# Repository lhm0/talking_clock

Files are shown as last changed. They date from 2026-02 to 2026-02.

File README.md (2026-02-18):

# Speaking Clock – Open Source Talking Clock for Visually Impaired Users

This repository is part of an open-source project for a simple, battery-powered **talking clock** designed for visually impaired and elderly users.

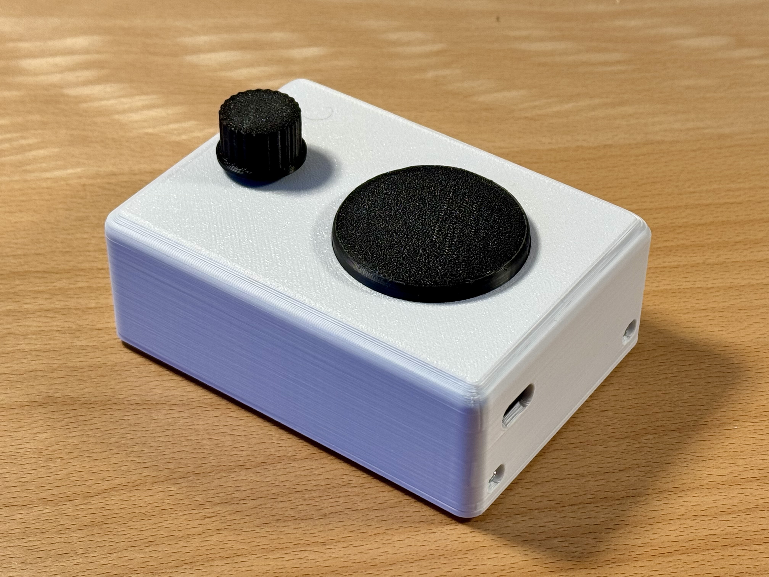
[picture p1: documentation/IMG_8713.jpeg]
Speaking Clock


The device announces the current time at the press of a button.  
If the button is pressed a second time within a short time window, it also announces the date.

Watch the full project video on YouTube:  
[Talking Clock – Demo & Build](https://youtu.be/vuX4cK3g9_s?si=J2-5so-r-MG_IsnX)

## Part of an Accessible Devices Collection

This repository is part of a small collection of **minimalistic, accessibility-focused devices for visually impaired users**. All projects follow a similar philosophy: simple operation, tactile or acoustic feedback, and a strong focus on usability and low power consumption.

The currently available devices in this collection are:

- **[DAB+ Radio](https://github.com/lhm0/DAB_minimalist)** – A minimalist, easy-to-use DAB+ radio  
- **[Talking Clock](https://github.com/lhm0/talking_clock)** – This project: a clock that announces the time acoustically  
- **[Accessible IR Remote Control](https://github.com/lhm0/accessible_ir_remote)** – A tactile, low-power TV remote control  

All projects are designed to be practical, easy to reproduce, and suitable for everyday use by visually impaired users.

## Design Goals

The main design goals of this project are:

- A **minimal and accessible user interface**
- **Fully offline operation** (no internet required)
- **Very low power consumption** for multi-year battery life
- **Simple configuration** using a smartphone via Wi-Fi
- **Low-cost hardware** based on breakout modules and a custom PCB
- A **3D-printed enclosure** for easy assembly

The clock is based on an ESP32-S3 microcontroller, uses a DS3231 real-time clock for accurate timekeeping, and plays pre-generated MP3 audio files through an I2S audio amplifier and a small speaker.  
To achieve extremely low standby power consumption, the entire system is powered only when an announcement is made.

All hardware design files, firmware, and related resources are open source and can be adapted or extended for your own projects.

---

## Time Announcement Audio Files

This repository contains **English time announcement audio files (MP3)** generated for use in the speaking clock and similar applications, systems, or projects.

These files are used as building blocks to construct spoken time and date announcements, for example:

- “The time is noon”
- “It’s one p.m.”
- “Today is Monday”

---

## License / Usage

The audio files in this repository were generated using **ttsMP3.com**.  
According to the ttsMP3 FAQ, these MP3 files may be used in personal and commercial projects without restriction (see: https://ttsmp3.com/faq).

The audio files can therefore be:

- Used in personal projects  
- Used in commercial projects  
- Shared and redistributed as part of other projects  

**Note:** This repository does not include or distribute any TTS software or voices themselves, only the generated audio files.

---

## About

These audio files are intended to be used as building blocks for English time announcements in embedded projects such as the Speaking Clock.

If you use this repository, please make sure to check the current terms of ttsMP3.com to ensure compliance with their conditions.

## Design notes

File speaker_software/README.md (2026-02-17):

# Speaker Software (ESP32-S3 Pico)

This folder contains the ESP32-S3 implementation.

## Structure

- `platformio.ini` - PlatformIO environments and build flags
- `src/` - Application entry point (`main.cpp`)
- `include/` - Project-wide config and board pin maps
- `lib/` - Reusable modules (hardware abstraction + device drivers)
- `test/` - Placeholder for unit tests
- `docs/` - Notes and integration docs

## Modules

- `lib/hal/` - Hardware abstraction interfaces
- `lib/time_speech/` - Time/date playlist generators + timezone/DST
- `lib/rtc_ds3231/` - DS3231 RTC driver

## Notes

- Audio files are stored in LittleFS under `/mp3`.
- Audio uses ESP8266Audio (legacy i2s.h backend).

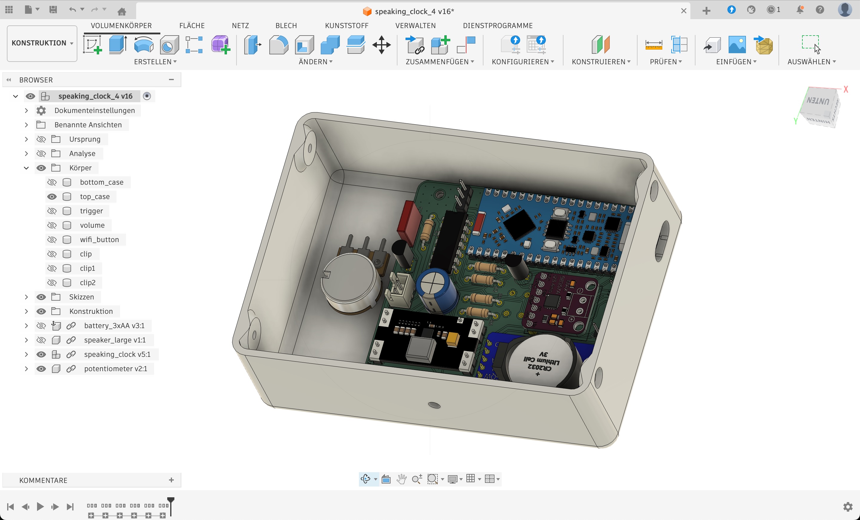
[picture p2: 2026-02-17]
documentation/mech_design3.jpg

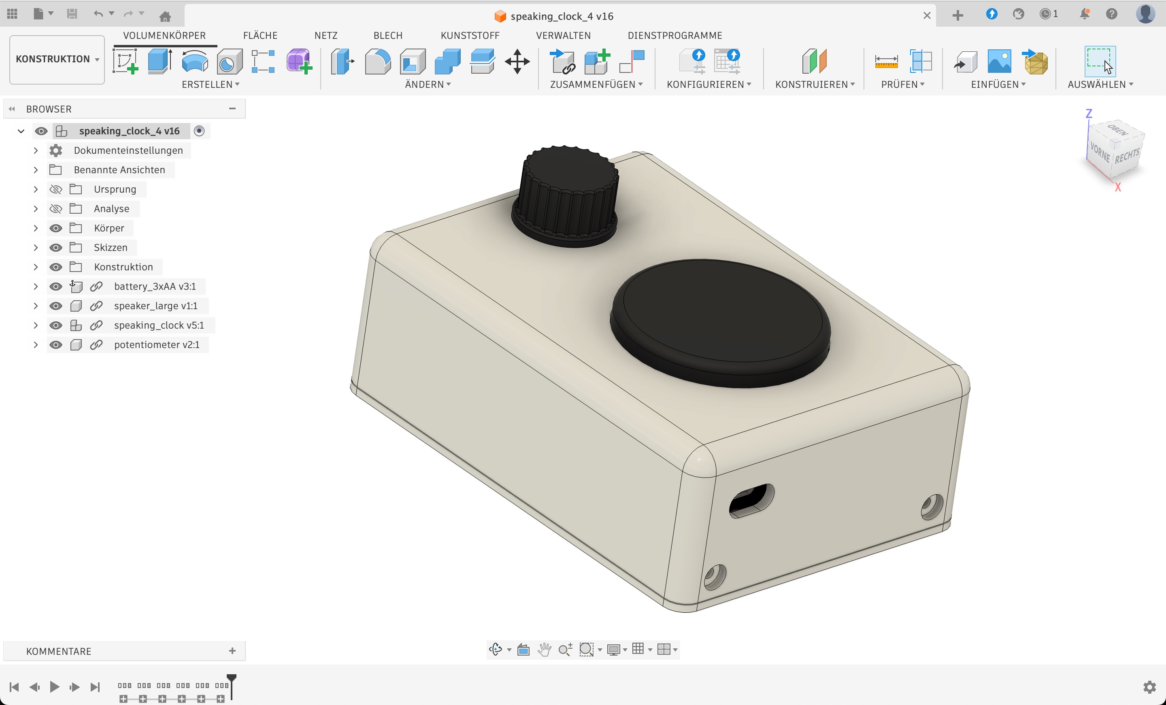
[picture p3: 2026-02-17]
documentation/mech_design1.jpg

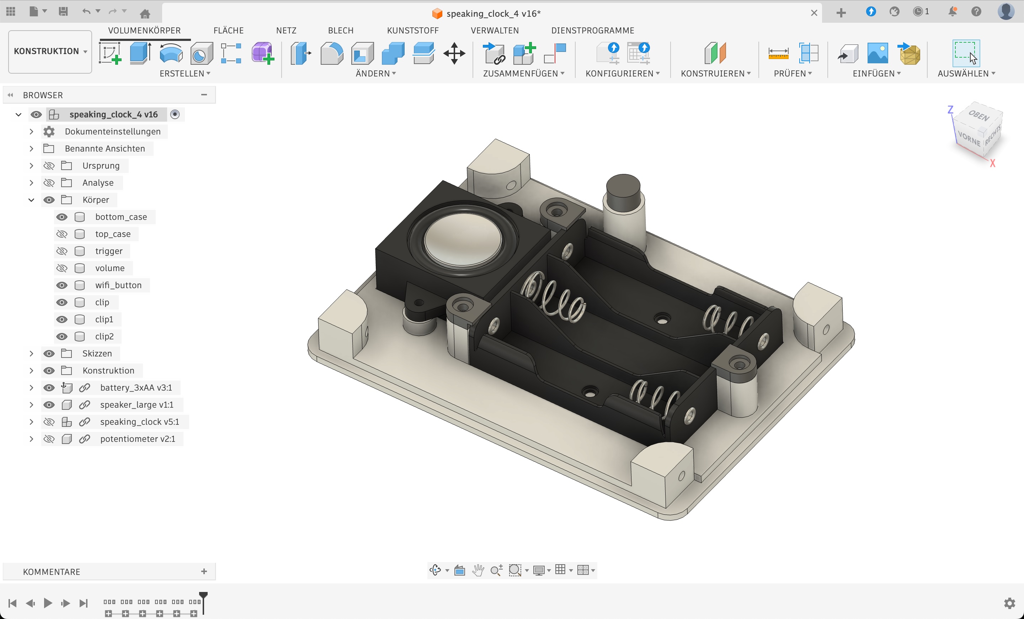
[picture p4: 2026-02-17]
documentation/mech_design2.jpg

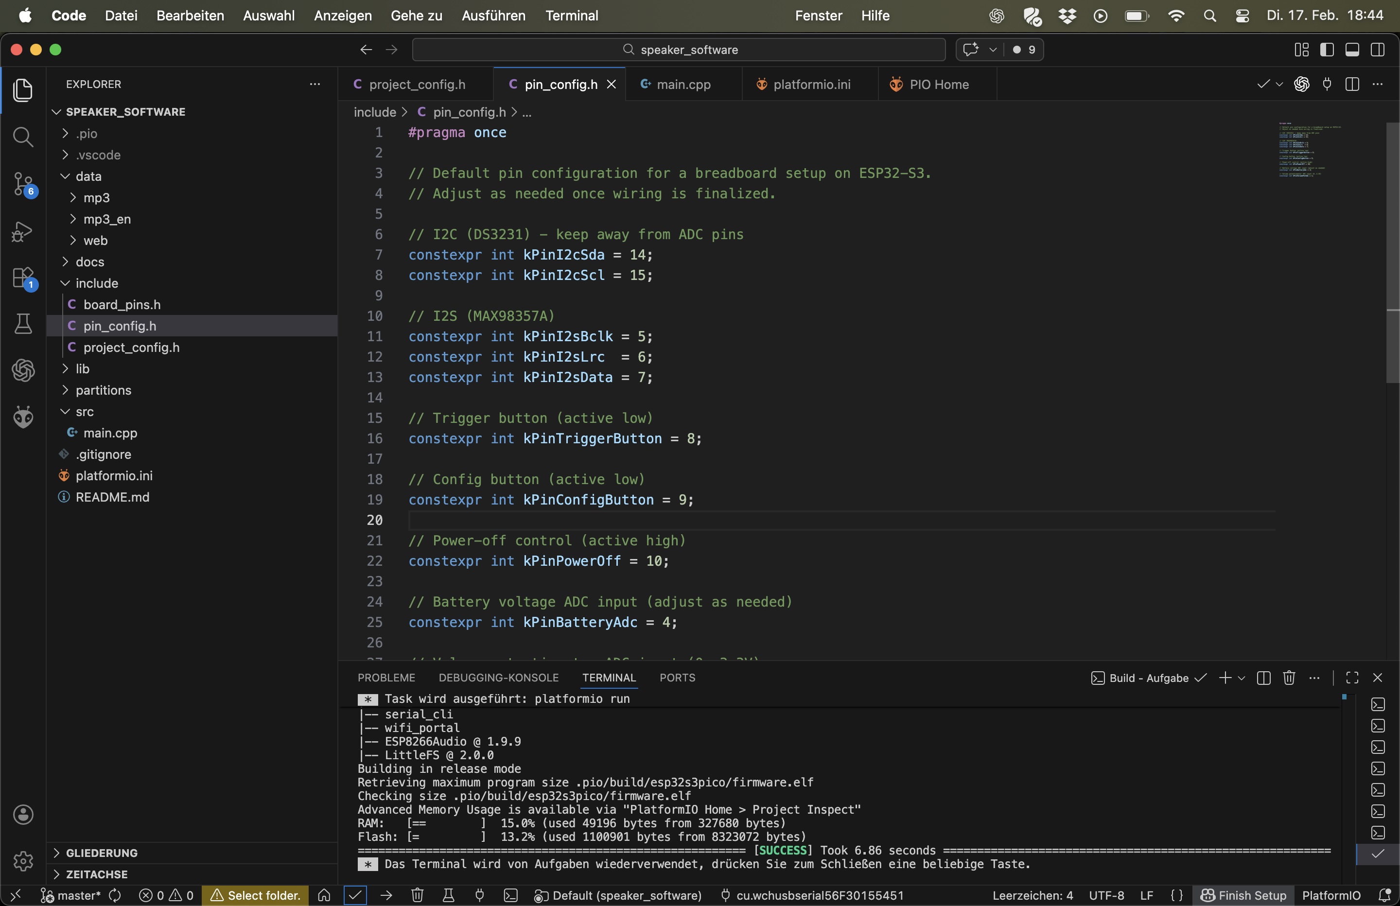
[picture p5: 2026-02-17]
documentation/VS_Code.jpg

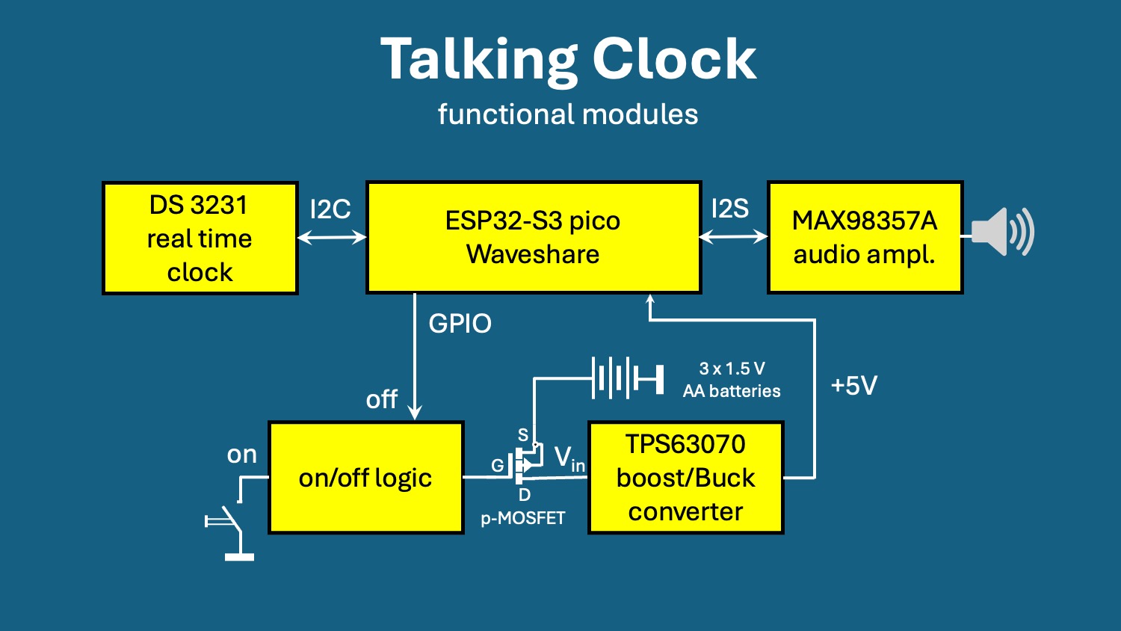
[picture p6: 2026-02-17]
documentation/functional blocks.jpg

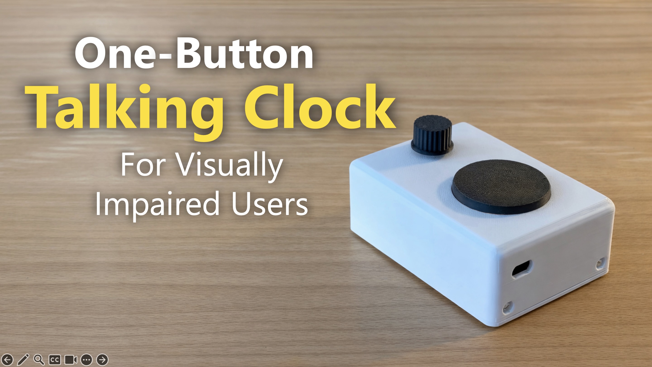
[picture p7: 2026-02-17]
documentation/thumbnail.jpg

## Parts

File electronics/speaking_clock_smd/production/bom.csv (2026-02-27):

Designator | Footprint | Quantity | Value | LCSC Part #
BT1 | Keytone_CR2032_holder | 1 | CR2032
C1, C10, C11, C13, C16, C19, C2, C24, C27, C29, C31, C8 | 0402 | 12 | 100nF | C307331
C12 | 0402 | 1 | 10nF | C15195
C14, C15, C17, C9 | 0402 | 4 | 1µF | C52923
C18, C22, C23, C3 | 0603 | 4 | 10µF | C96446
C20, C21, C30 | 0805 | 3 | 10µF | C15850
C25, C26 | 0805 | 2 | 22µF | C45783
C28 | 0603 | 1 | 1nF | C1588
C4, C6 | 0402 | 2 | 10pF | C32949
C5, C7 | 0402 | 2 | 3p3 | C1565
D1, D2 | D_SMA | 2 | SS24 | C7420362
D3 | 0603 | 1 | LED | C2286
J1 | USB_C_Receptacle | 1 | USB_C_Receptacle_USB2.0 | C709357
J2 | JST_XH_B2B-XH-A_1x02_P2.50mm_Vertical | 1 | Conn_01x02_Pin
J3 | 3_pin_jumper | 1 | Conn_01x03_Pin
J4 | 2_pin | 1 | Conn_01x02_Pin
L1, L2 | 0402 | 2 | 2n2 | C412264
L3 | L_Bourns_SRP7028A_7.3x6.6mm | 1 | 2.2µH | C167218
Q1 | SOT-23 | 1 | IRLML6401 | C382329
Q2, Q3 | SOT-23 | 2 | AO3400A | C20917
R1, R2 | 0402 | 2 | 5k1 | C25905
R10, R11, R12, R13, R17, R18, R19 | 0402 | 7 | 10k | C25744
R14 | 0402 | 1 | 20k | C25765
R15, R16 | 0402 | 2 | 4k7 | C25900
R20, R21, R22, R23, R28, R3 | 0402 | 6 | 100k | C25741
R24 | 0603 | 1 | 470k | C23178
R25 | 0603 | 1 | 150k | C22807
R26 | 0603 | 1 | 1k | C21190
R27 | 0402 | 1 | 2k2 | C25879
R4, R5, R6, R7, R8 | 0402 | 5 | 0 | C17168
R9 | 0402 | 1 | 22 | C25092
SW1 | C720477 | 1 | reset | C720477
SW2 | RotaryEncoder_Alps_EC11E-Switch_Vertical_H20mm | 1 | volume_knob
SW3 | OmronTaster | 1 | config
U1 | SOIC-8_5.3x5.3mm_P1.27mm | 1 | W25Q128JVS | C97521
U2 | SOT-23-6 | 1 | USBLC6-2SC6 | C2687116
U20, U21, U22 | JLC_tooling_hole | 3 | ~
U3 | PCB_antenna | 1 | WiFi antenna
U4 | IC_ESP32-S3 | 1 | ESP32-S3 | C2913192
U5 | 1pin | 1 | ~
U6 | SOIC-14_3.9x8.7mm_P1.27mm | 1 | HEF4093B | C7867
U7 | VREG_TPS63070RNMR | 1 | TPS63070RNMR | C109322
U8 | SOIC-8_3.9x4.9mm_P1.27mm | 1 | DS3231MZ | C107410
U9 | TQFN-16-1EP_3x3mm_P0.5mm_EP1.23x1.23mm | 1 | MAX98357A | C910544
Y1 | Crystal_SMD_4Pin_3.2x2.5mm | 1 | 40 MHz | C379787

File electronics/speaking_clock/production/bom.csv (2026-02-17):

Designator | Footprint | Quantity | Value | LCSC Part #
A1 | Waveshare_ESP32_S3_pico | 1 | Waveshare_ESP32-S3_Pico
C1 | CP_Radial_D6.3mm_P2.50mm | 1 | 220µF, 16V
C2, C3 | C_Rect_L10.0mm_W2.5mm_P7.50mm_MKS4 | 2 | 100nF
D1 | LED_D3.0mm | 1 | LED
J1 | JST_XH_B2B-XH-A_1x02_P2.50mm_Vertical | 1 | Conn_01x02_Pin
J2, J4 | 3_pin_jumper | 2 | Conn_01x03_Pin
J3 | 2_pin | 1 | Conn_01x02_Pin
Q1, Q2 | TO-92L_Inline | 2 | 2N7000
Q3 | SOT-23 | 1 | IRLML6401
R1, R2, R3 | R_Axial_DIN0207_L6.3mm_D2.5mm_P10.16mm_Horizontal | 3 | 100k | C25768
R4 | R_Axial_DIN0207_L6.3mm_D2.5mm_P10.16mm_Horizontal | 1 | 1k
R5 | R_Axial_DIN0207_L6.3mm_D2.5mm_P10.16mm_Horizontal | 1 | 1M
R6 | R_Axial_DIN0207_L6.3mm_D2.5mm_P10.16mm_Horizontal | 1 | 2M
SW1 | OmronTaster | 1 | ON
SW2 | OmronTaster | 1 | config
U1 | TPS63070_breakout | 1 | TPS63070
U2 | DIP-14_W7.62mm | 1 | HEF4093B
U3 | MAX98357A_breakout | 1 | MAX98357A
U4 | DS3231 | 1 | DS3231

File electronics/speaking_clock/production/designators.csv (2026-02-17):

A1:1
C1:1
C2:1
C3:1
D1:1
J1:1
J2:1
J3:1
J4:1
Q1:1
Q2:1
Q3:1
R1:1
R2:1
R3:1
R4:1
R5:1
R6:1
SW1:1
SW2:1
U1:1
U2:1
U3:1
U4:1

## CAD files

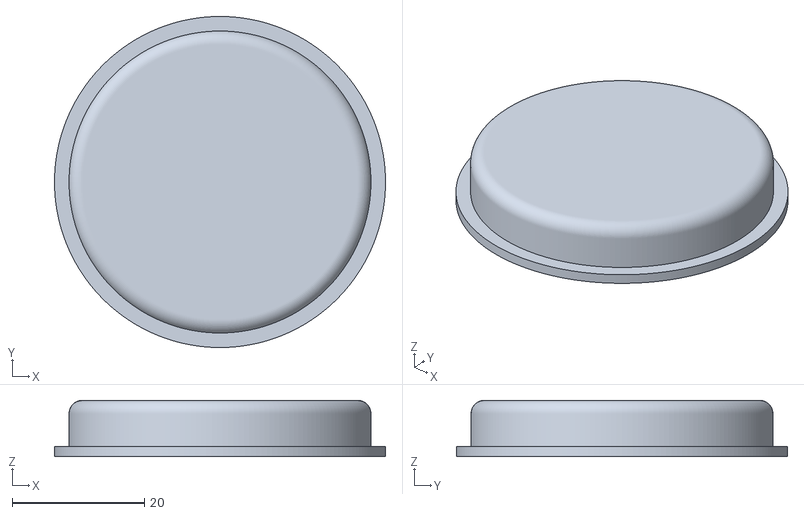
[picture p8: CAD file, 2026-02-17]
mechanical_design/trigger.stl
50.0 x 50.0 x 8.50

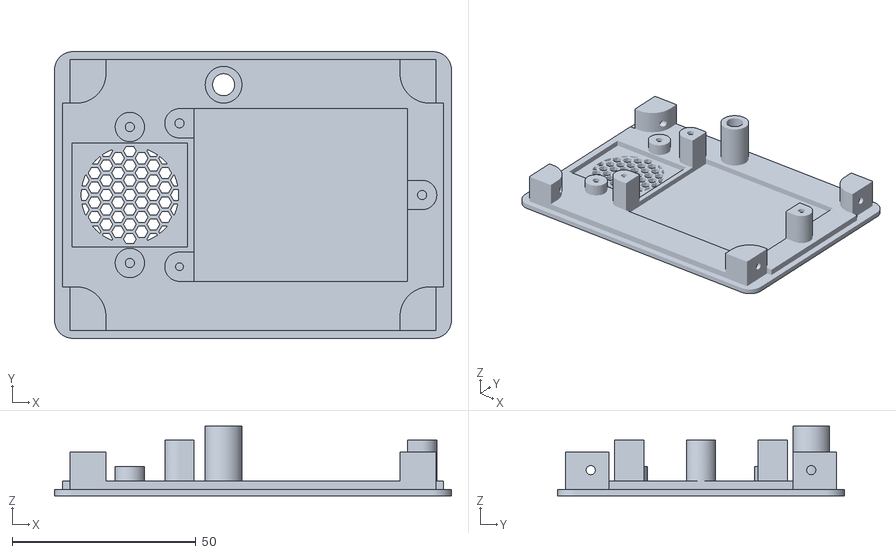
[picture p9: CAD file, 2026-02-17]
mechanical_design/bottom_case.stl
108.0 x 78.0 x 19.0

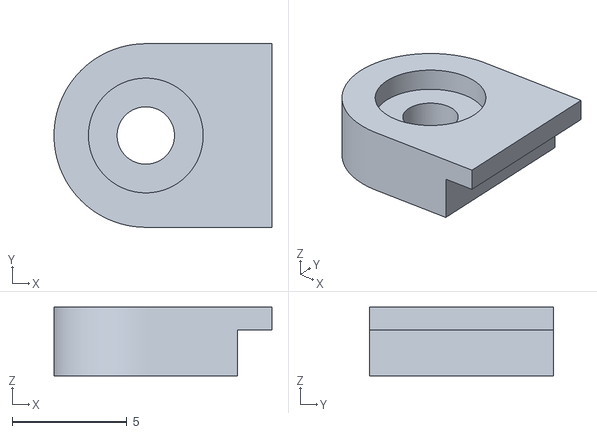
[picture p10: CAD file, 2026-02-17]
mechanical_design/clip2.stl
9.50 x 8.00 x 3.00

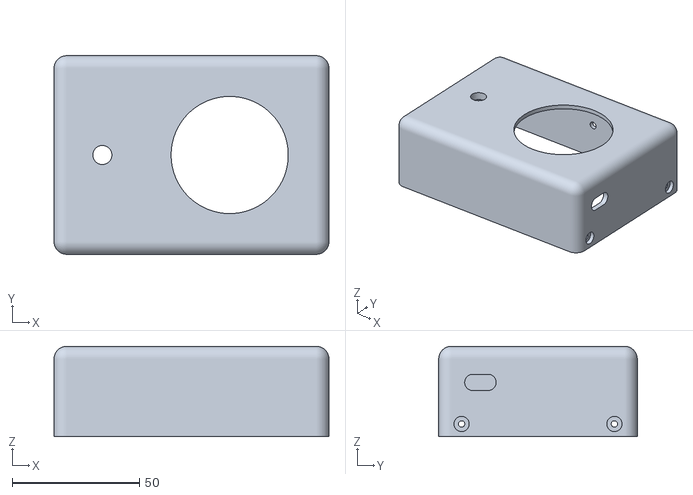
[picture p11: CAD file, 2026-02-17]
mechanical_design/top_case.stl
108.0 x 78.0 x 35.5

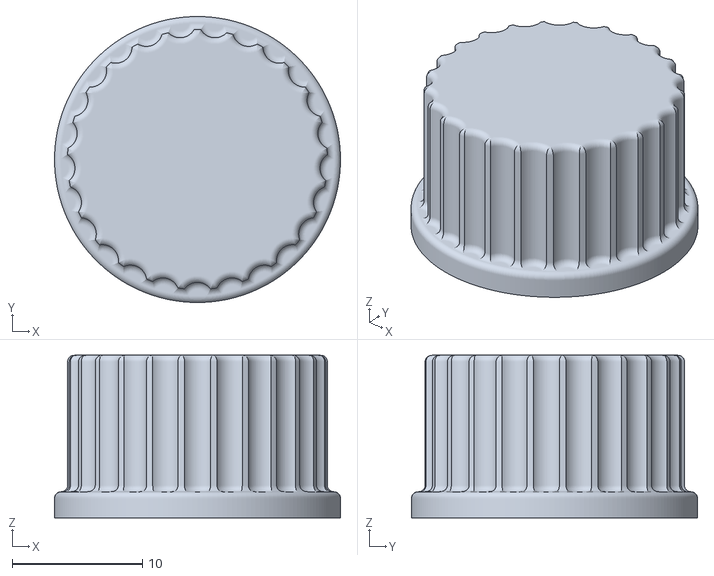
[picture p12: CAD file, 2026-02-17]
mechanical_design/volume.stl
22.0 x 22.0 x 12.5

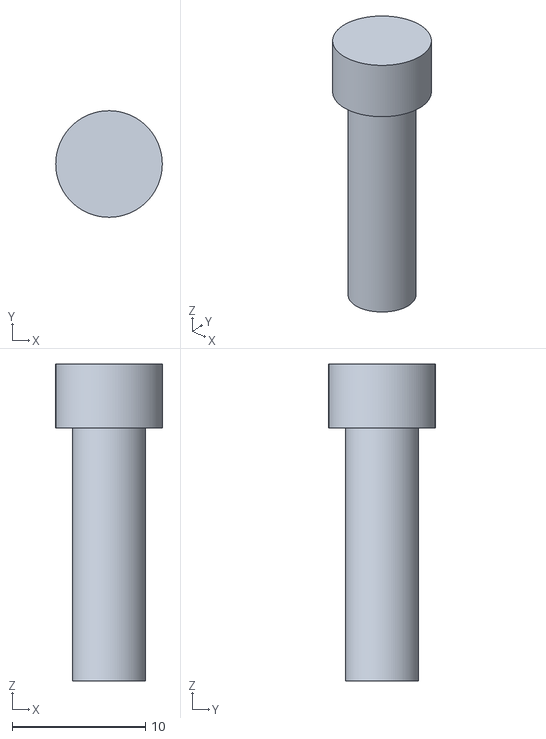
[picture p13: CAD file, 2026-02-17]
mechanical_design/wifi_button.stl
8.00 x 8.00 x 23.8

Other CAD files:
mechanical_design/clip1.stl
mechanical_design/clip.stl

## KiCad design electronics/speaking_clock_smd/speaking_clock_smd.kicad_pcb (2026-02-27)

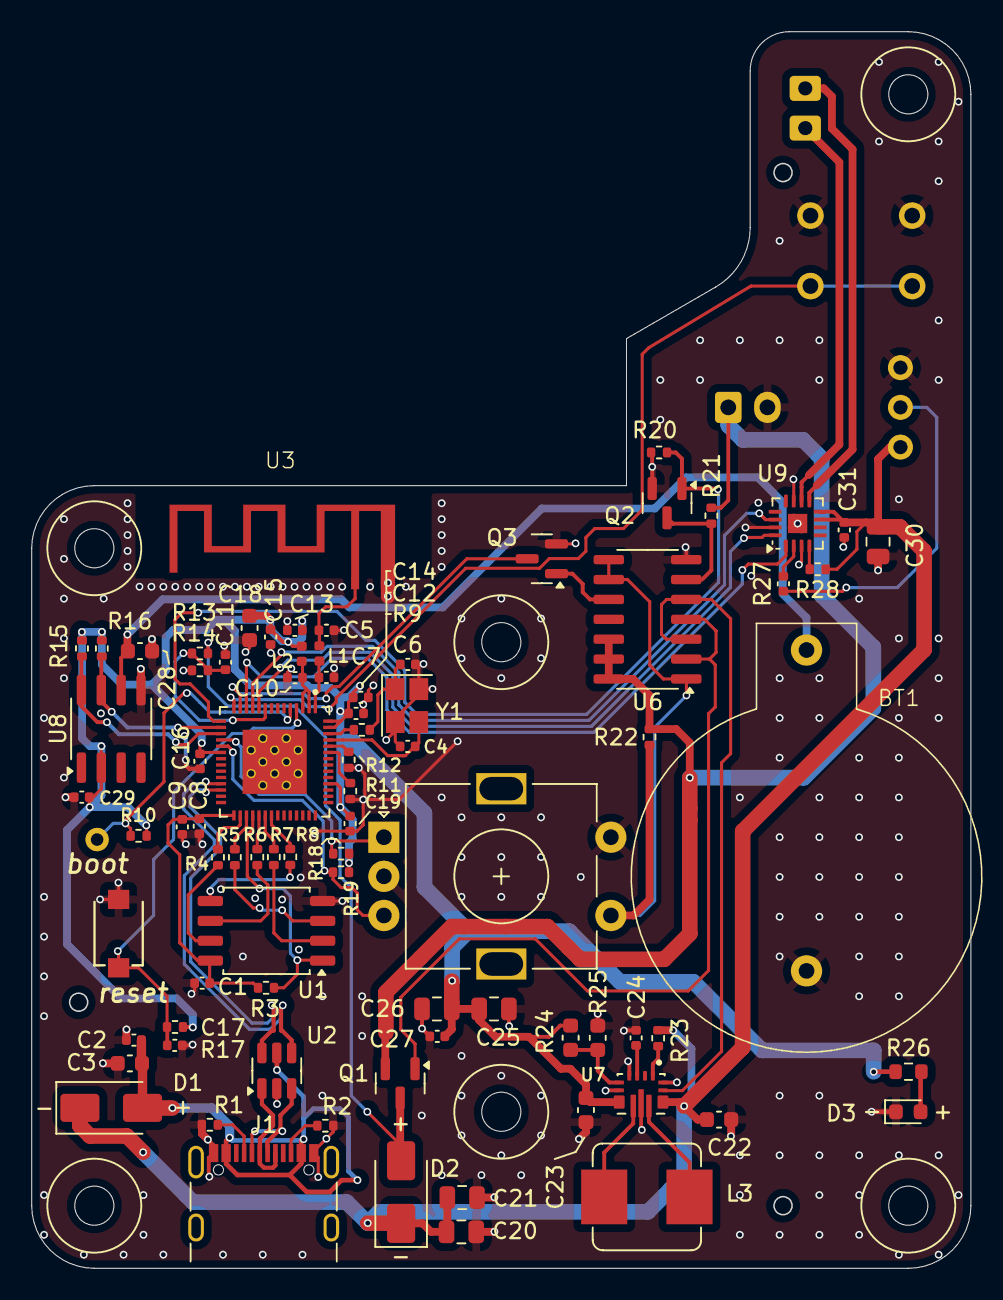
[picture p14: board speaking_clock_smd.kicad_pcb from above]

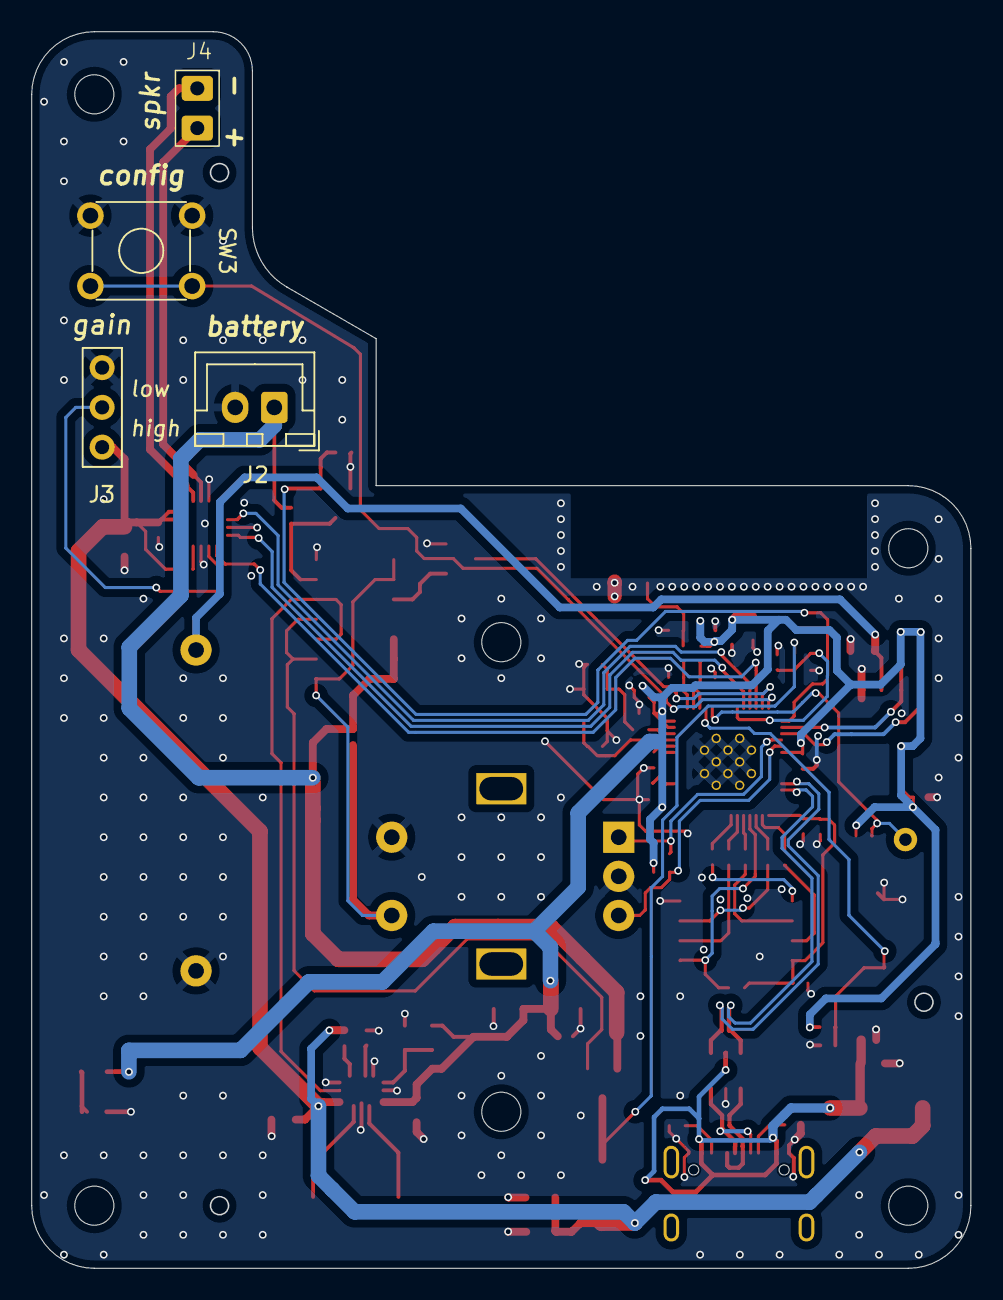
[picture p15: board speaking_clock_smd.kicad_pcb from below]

Board: 4 copper layers, 60.0 x 79.0 mm, 89 parts (4 on the bottom side), 62 nets.

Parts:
BT1: CR2032; Keytone_CR2032_holder
C1, C2, C8, C10, C11, C13, C16, C19, C24, C27, C29, C31: 100nF; C_0402_1005Metric
C3, C18, C22, C23: 10µF; C_0603_1608Metric
C4, C6: 10pF; C_0402_1005Metric
C5, C7: 3p3; C_0402_1005Metric
C9, C14, C15, C17: 1µF; C_0402_1005Metric
C12: 10nF; C_0402_1005Metric
C20, C21, C30: 10µF; C_0805_2012Metric
C25, C26: 22µF; C_0805_2012Metric
C28: 1nF; C_0603_1608Metric
D1, D2: SS24; D_SMA
D3: LED; LED_0603_1608Metric
J1: USB_C_Receptacle_USB2.0; USB_C_Receptacle
J2: Conn_01x02_Pin; JST_XH_B2B-XH-A_1x02_P2.50mm_Vertical
J3: Conn_01x03_Pin; 3_pin_jumper
J4: Conn_01x02_Pin; 2_pin
L1, L2: 2n2; L_0402_1005Metric
L3: 2.2µH; L_Bourns_SRP7028A_7.3x6.6mm
Q1: IRLML6401; SOT-23
Q2, Q3: AO3400A; SOT-23
R1, R2: 5k1; R_0402_1005Metric
R3, R20, R21, R22, R23, R28: 100k; R_0402_1005Metric
R4, R5, R6, R7, R8: 0; R_0402_1005Metric
R9: 22; R_0402_1005Metric
R10, R11, R12, R13, R17, R18, R19: 10k; R_0402_1005Metric
R14: 20k; R_0402_1005Metric
R15, R16: 4k7; R_0402_1005Metric
R24: 470k; C_0603_1608Metric
R25: 150k; C_0603_1608Metric
R26: 1k; R_0603_1608Metric
R27: 2k2; C_0402_1005Metric
SW1: reset; C720477
SW2: volume_knob; RotaryEncoder_Alps_EC11E-Switch_Vertical_H20mm
SW3: config; OmronTaster
U1: W25Q128JVS; SOIC-8_5.3x5.3mm_P1.27mm
U2: USBLC6-2SC6; SOT-23-6
U3: WiFi antenna; PCB_antenna
U4: ESP32-S3; IC_ESP32-S3
U5: 1pin
U6: HEF4093B; SOIC-14_3.9x8.7mm_P1.27mm
U7: TPS63070RNMR; VREG_TPS63070RNMR
U8: DS3231MZ; SOIC-8_3.9x4.9mm_P1.27mm
U9: MAX98357A; TQFN-16-1EP_3x3mm_P0.5mm_EP1.23x1.23mm
U20, U21, U22: JLC_tooling_hole
Y1: 40 MHz; Crystal_SMD_4Pin_3.2x2.5mm

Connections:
+3.3V: C12.1, C13.1, C14.1, C15.1, C16.1, C18.1, C19.1, C23.2, C25.1, C26.1, C27.1, C29.1, L2.2, R10.2, R15.2, R16.2, R17.1, R18.2, R19.1, R24.1, R26.1, U4.20 (VDD3P3_RTC), U4.46 (VDD3P3_CPU), U4.55 (VDDA1), U4.56 (VDDA2), U7.7_8 (VOUT), U8.2 (VCC)
/ESP32-S3 microcontroller/A5: J1.A5 (CC1), R1.1
/ESP32-S3 microcontroller/B5: J1.B5 (CC2), R2.1
/ESP32-S3 microcontroller/EN: C17.1, R17.2, SW1.1, U4.4 (CHIP_PU)
/ESP32-S3 microcontroller/ESP_D+: J1.A6 (D+), J1.B6 (D+), U2.1 (I/O1)
/ESP32-S3 microcontroller/ESP_D-: J1.A7 (D-), J1.B7 (D-), U2.3 (I/O2)
/ESP32-S3 microcontroller/GPIO4: C11.1, R13.2, R14.1, U4.9 (GPIO4)
/ESP32-S3 microcontroller/GPIO45: R11.1, U4.51 (GPIO45)
/ESP32-S3 microcontroller/GPIO46: R12.1, U4.52 (GPIO46)
/ESP32-S3 microcontroller/LNA: C7.1, L1.2, U4.1 (LNA_IN)
/ESP32-S3 microcontroller/SPICLK: R6.1, U1.6 (CLK)
/ESP32-S3 microcontroller/SPICLK_: R6.2, U4.33 (SPICLK)
/ESP32-S3 microcontroller/SPICS0: R3.1, U1.1 (~CS), U4.32 (SPICS0)
/ESP32-S3 microcontroller/SPID: R8.1, U1.5 (DI(IO0))
/ESP32-S3 microcontroller/SPID_: R8.2, U4.35 (SPID)
/ESP32-S3 microcontroller/SPIHD: R4.1, U1.7 (IO3)
/ESP32-S3 microcontroller/SPIHD_: R4.2, U4.30 (SPIHD)
/ESP32-S3 microcontroller/SPIQ: R7.1, U1.2 (DO(IO1))
/ESP32-S3 microcontroller/SPIQ_: R7.2, U4.34 (SPIQ)
/ESP32-S3 microcontroller/SPIWP: R5.1, U1.3 (IO2)
/ESP32-S3 microcontroller/SPIWP_: R5.2, U4.31 (SPIWP)
/ESP32-S3 microcontroller/UD_ESP+: U2.6 (I/O1), U4.26 (GPIO20)
/ESP32-S3 microcontroller/UD_ESP-: U2.4 (I/O2), U4.25 (GPIO19)
/ESP32-S3 microcontroller/VBUS3: C2.2, C3.1, D1.2 (A), J1.A4 (VBUS), J1.A9 (VBUS), J1.B4 (VBUS), J1.B9 (VBUS), U2.5 (VBUS)
/ESP32-S3 microcontroller/VDD3P3: C10.1, L2.1, U4.2 (VDD3P3), U4.3 (VDD3P3)
/ESP32-S3 microcontroller/VDD_SPI: C1.2, C8.1, C9.1, R3.2, U1.8 (VCC), U4.29 (VDD_SPI)
/ESP32-S3 microcontroller/XTAL_N: C4.1, U4.53 (XTAL_N), Y1.3
/ESP32-S3 microcontroller/XTAL_P: R9.2, U4.54 (XTAL_P)
/ESP32-S3 microcontroller/XTAL_Pp: C6.1, R9.1, Y1.1
/ESP32-S3 microcontroller/boot: R10.1, U4.5 (GPIO0), U5.1 (pin)
/ESP32-S3 microcontroller/feed: C5.1, L1.1, U3.2 (feed)
/peripherals/FB: R24.2, R25.1, U7.5 (FB)
/peripherals/Gain: R27.2, U9.2 (GAIN_SLOT)
/peripherals/Gain_Jumper: J3.2, R27.1
/peripherals/L1: L3.2, U7.11 (L1)
/peripherals/L2: L3.1, U7.9 (L2)
/peripherals/PS/SYNC: R23.2, U7.1 (PS/SYNC)
/peripherals/VAUX: C24.2, U7.3 (VAUX)
/peripherals/spkr_+: J4.2, U9.10 (OUTN)
/peripherals/spkr_-: J4.1, U9.9 (OUTP)
/peripherals//OFF: Q2.3 (D), R21.1, U6.6
/peripherals//ON: Q3.1 (G), U6.10
/peripherals//SD: R28.1, U9.4 (~SD_MODE)
GND: BT1.2 (-), C1.1, C2.1, C3.2, C4.2, C5.2, C6.2, C7.2, C8.2, C9.2, C10.2, C11.2, C12.2, C13.2, C14.2, C15.2, C16.2, C17.2, C18.2, C19.2, C20.2, C21.2, C22.1, C23.1, C24.1, C25.2, C26.2, C27.2, C28.1, C29.2, C30.2, C31.2, D3.1 (K), J1.A1 (GND), J1.A12 (GND), J1.B1 (GND), J1.B12 (GND), J2.2, J3.3, Q2.2 (S), Q3.2 (S), R1.2, R2.2, R11.2, R12.2, R14.2, R20.1, R25.2, SW1.2, SW2.C, SW2.S2, SW3.1 (A), U1.4 (GND), U2.2 (GND), U3.1 (GND), U4.57 (GND), U4.58 (GND), U4.59 (GND), U4.60 (GND), U4.61 (GND), U4.62 (GND), U4.63 (GND), U4.64 (GND), U4.65 (GND), U4.66 (GND), U4.67 (GND), U4.68 (GND), U4.69 (GND), U6.7 (GND), U7.4 (GND), U7.6 (FB2), U7.10 (PGND), U7.15 (VSEL), U8.5 (GND), U9.3 (GND), U9.11 (GND), U9.15 (GND), U9.17 (PAD), Y1.2, Y1.4
I2C_SCL: R15.1, U4.17 (GPIO12), U8.8 (SCL)
I2C_SDA: R16.1, U4.16 (GPIO11), U8.7 (SDA)
I2S_BCLK: U4.10 (GPIO5), U9.16 (BCLK)
I2S_DIN: U4.12 (GPIO7), U9.1 (DIN)
I2S_LRC: U4.11 (GPIO6), U9.14 (LRCLK)
unnamed: BT1.1 (+), C28.2, U8.6 (VBAT)
unnamed: D3.2 (A), R26.2
OFF: Q2.1 (G), R20.2, U4.15 (GPIO10)
ON: R22.1, SW2.S1, U6.1, U6.8, U6.9
VBat: J2.1, Q1.2 (S), R21.2, R22.2, U6.12, U6.13, U6.14 (VCC)
VBat_s: D2.2 (A), Q1.3 (D), R13.1
VIN: C20.1, C21.1, C22.2, C30.1, C31.1, D1.1 (K), D2.1 (K), J3.1, R23.1, R28.2, U7.12_13 (VIN), U9.7 (VDD), U9.8 (VDD)
config: SW3.2 (B), U4.14 (GPIO9)
enable: U6.3, U6.5, U7.14 (EN)
rotary_A: R18.1, SW2.A, U4.18 (GPIO13)
rotary_B: R19.2, SW2.B, U4.19 (GPIO14)
trigger: Q3.3 (D), U4.13 (GPIO8)
/enable: Q1.1 (G), U6.2, U6.4

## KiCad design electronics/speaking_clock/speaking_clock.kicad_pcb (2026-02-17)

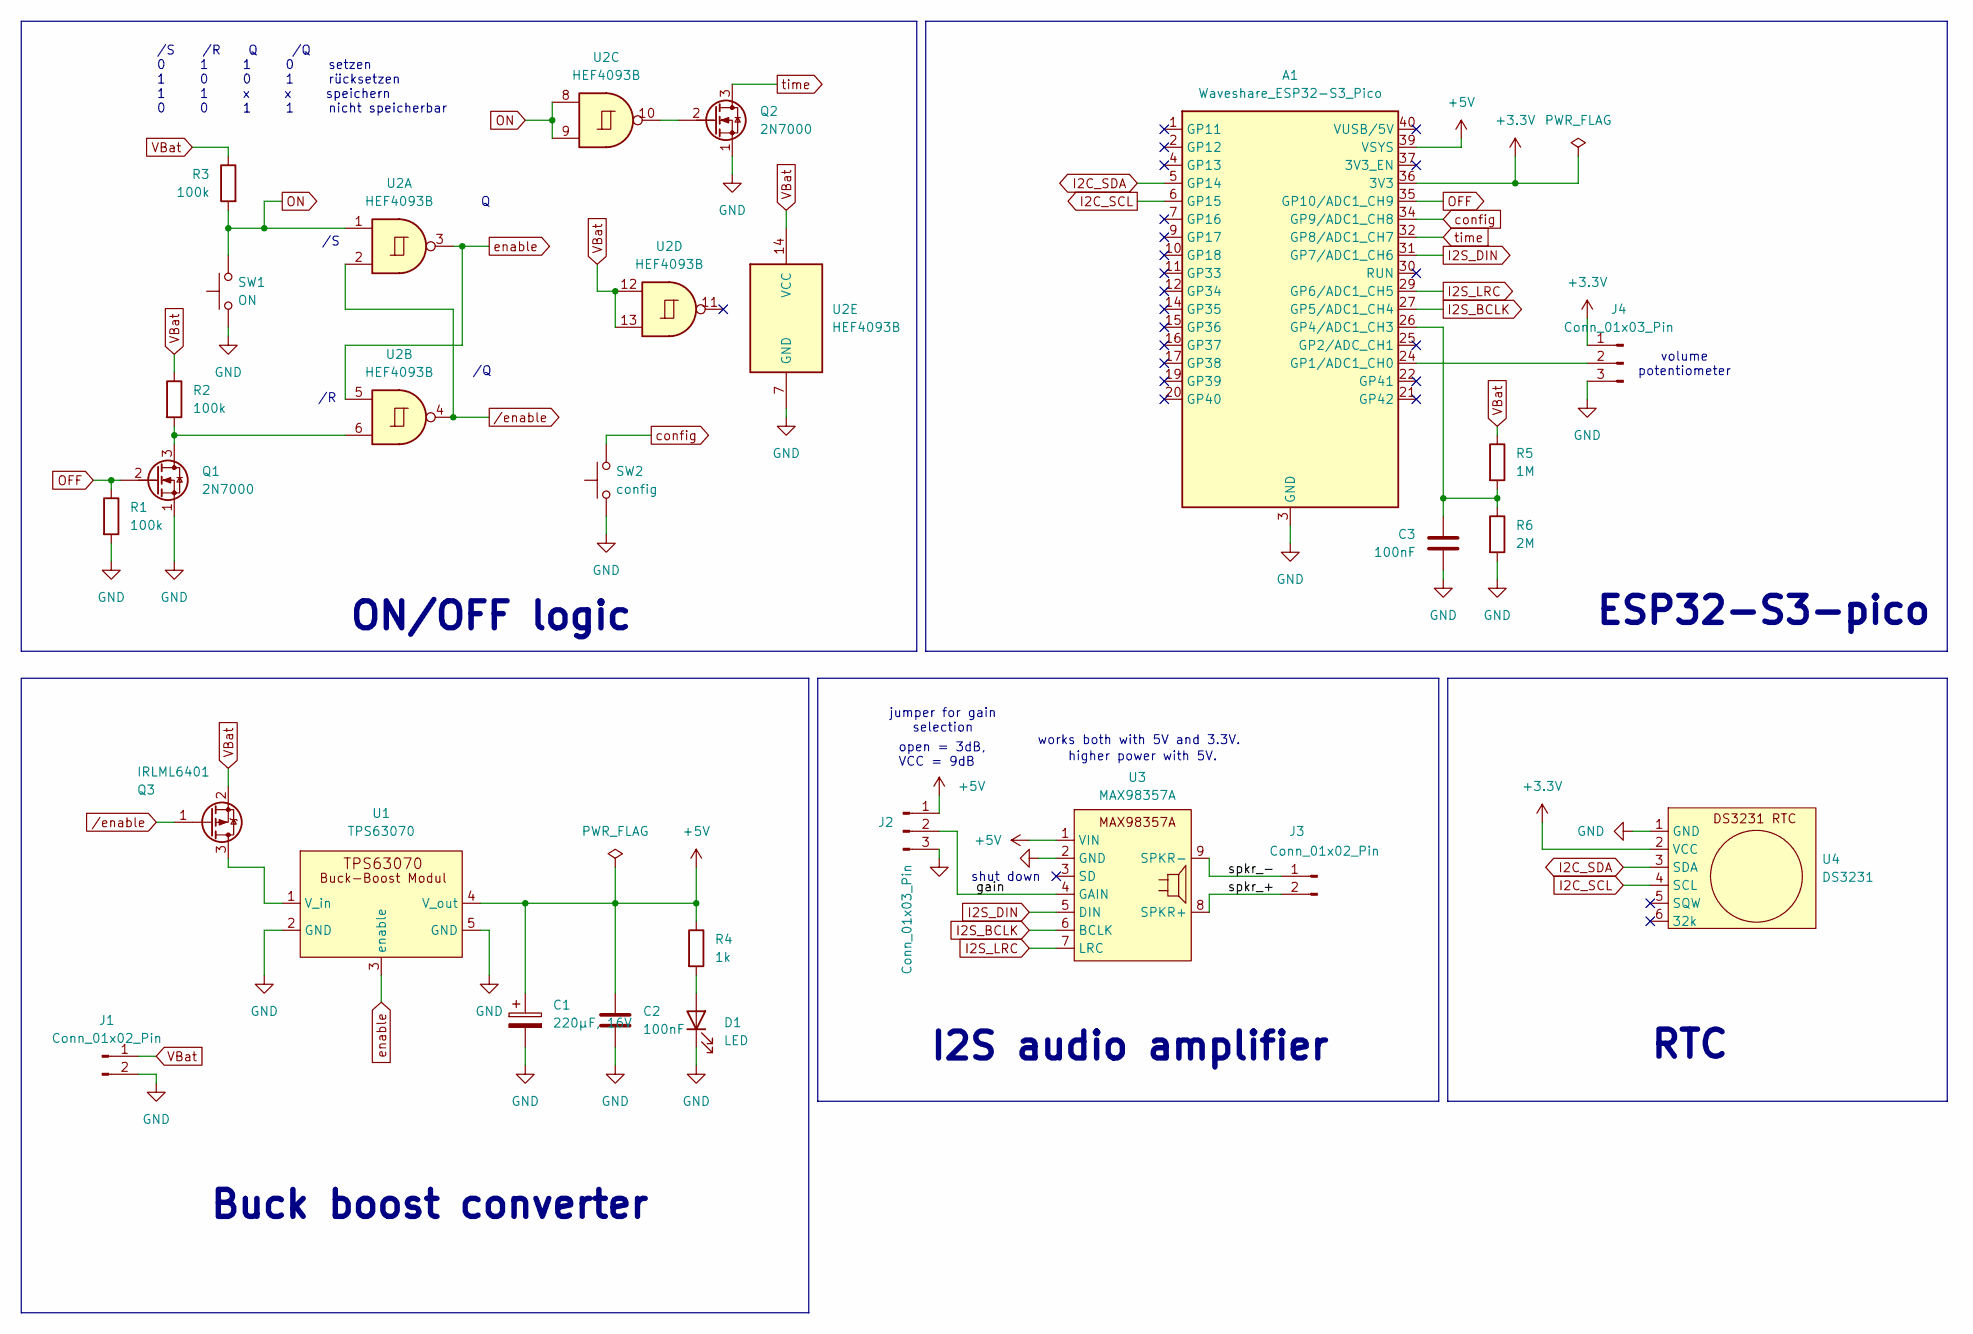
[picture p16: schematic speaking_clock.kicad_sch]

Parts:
A1: Waveshare_ESP32-S3_Pico; Waveshare_ESP32_S3_pico
C1: 220µF, 16V; CP_Radial_D6.3mm_P2.50mm
C2, C3: 100nF; C_Rect_L10.0mm_W2.5mm_P7.50mm_MKS4
D1: LED; LED_D3.0mm
J1: Conn_01x02_Pin; JST_XH_B2B-XH-A_1x02_P2.50mm_Vertical
J2, J4: Conn_01x03_Pin; 3_pin_jumper
J3: Conn_01x02_Pin; 2_pin
Q1, Q2: 2N7000; TO-92L_Inline
Q3: IRLML6401; SOT-23
R1, R2, R3: 100k; R_Axial_DIN0207_L6.3mm_D2.5mm_P10.16mm_Horizontal; LCSC C25768
R4: 1k; R_Axial_DIN0207_L6.3mm_D2.5mm_P10.16mm_Horizontal
R5: 1M; R_Axial_DIN0207_L6.3mm_D2.5mm_P10.16mm_Horizontal
R6: 2M; R_Axial_DIN0207_L6.3mm_D2.5mm_P10.16mm_Horizontal
SW1: ON; OmronTaster
SW2: config; OmronTaster
U1: TPS63070; TPS63070_breakout
U2: HEF4093B; DIP-14_W7.62mm
U3: MAX98357A; MAX98357A_breakout
U4: DS3231

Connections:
+3.3V: A1.36 (3V3), J4.1, U4.2 (VCC), U4.9 (VCC)
+5V: A1.39 (VSYS), C1.1, C2.1, J2.1, R4.1, U1.4 (V_out), U3.1 (VIN)
/gain: J2.2, U3.4 (GAIN)
/spkr_+: J3.2, U3.8 (SPKR+)
/spkr_-: J3.1, U3.9 (SPKR-)
GND: A1.3 (GND), A1.8 (GND), A1.13 (GND), A1.18 (GND), A1.23 (GND), A1.28 (GND), A1.33 (GND), A1.38 (GND), C1.2, C2.2, C3.2, D1.1 (K), J1.2, J2.3, J4.3, Q1.1 (S), Q2.1 (S), R1.2, R6.2, SW1.1 (A), SW2.1 (A), U1.2 (GND), U1.5 (GND), U2.7 (GND), U3.2 (GND), U4.1 (GND), U4.10 (GND)
I2C_SCL: A1.6 (GP15), U4.4 (SCL), U4.7 (SCL)
I2C_SDA: A1.5 (GP14), U4.3 (SDA), U4.8 (SDA)
I2S_BCLK: A1.27 (GP5/ADC1_CH4), U3.6 (BCLK)
I2S_DIN: A1.31 (GP7/ADC1_CH6), U3.5 (DIN)
I2S_LRC: A1.29 (GP6/ADC1_CH5), U3.7 (LRC)
unnamed: A1.24 (GP1/ADC1_CH0), J4.2
unnamed: A1.26 (GP4/ADC1_CH3), C3.1, R5.2, R6.1
unnamed: D1.2 (A), R4.2
unnamed: Q1.3 (D), R2.2, U2.6
unnamed: Q2.2 (G), U2.10
unnamed: Q3.3 (D), U1.1 (V_in)
OFF: A1.35 (GP10/ADC1_CH9), Q1.2 (G), R1.1
ON: R3.2, SW1.2 (B), U2.1, U2.8, U2.9
VBat: J1.1, Q3.2 (S), R2.1, R3.1, R5.1, U2.12, U2.13, U2.14 (VCC)
config: A1.34 (GP9/ADC1_CH8), SW2.2 (B)
enable: U1.3 (enable), U2.3, U2.5
time: A1.32 (GP8/ADC1_CH7), Q2.3 (D)
/enable: Q3.1 (G), U2.2, U2.4

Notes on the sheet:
/S /R Q /Q 0 1 1 0 setzen 1 0 0 1 rücksetzen 1 1 x x speichern 0 0 1 1 nicht speicherbar
open = 3dB, VCC = 9dB
I2S audio amplifier
ESP32-S3-pico
jumper for gain selection
works both with 5V and 3.3V.
RTC
higher power with 5V.
Buck boost converter
shut down
ON/OFF logic
volume potentiometer

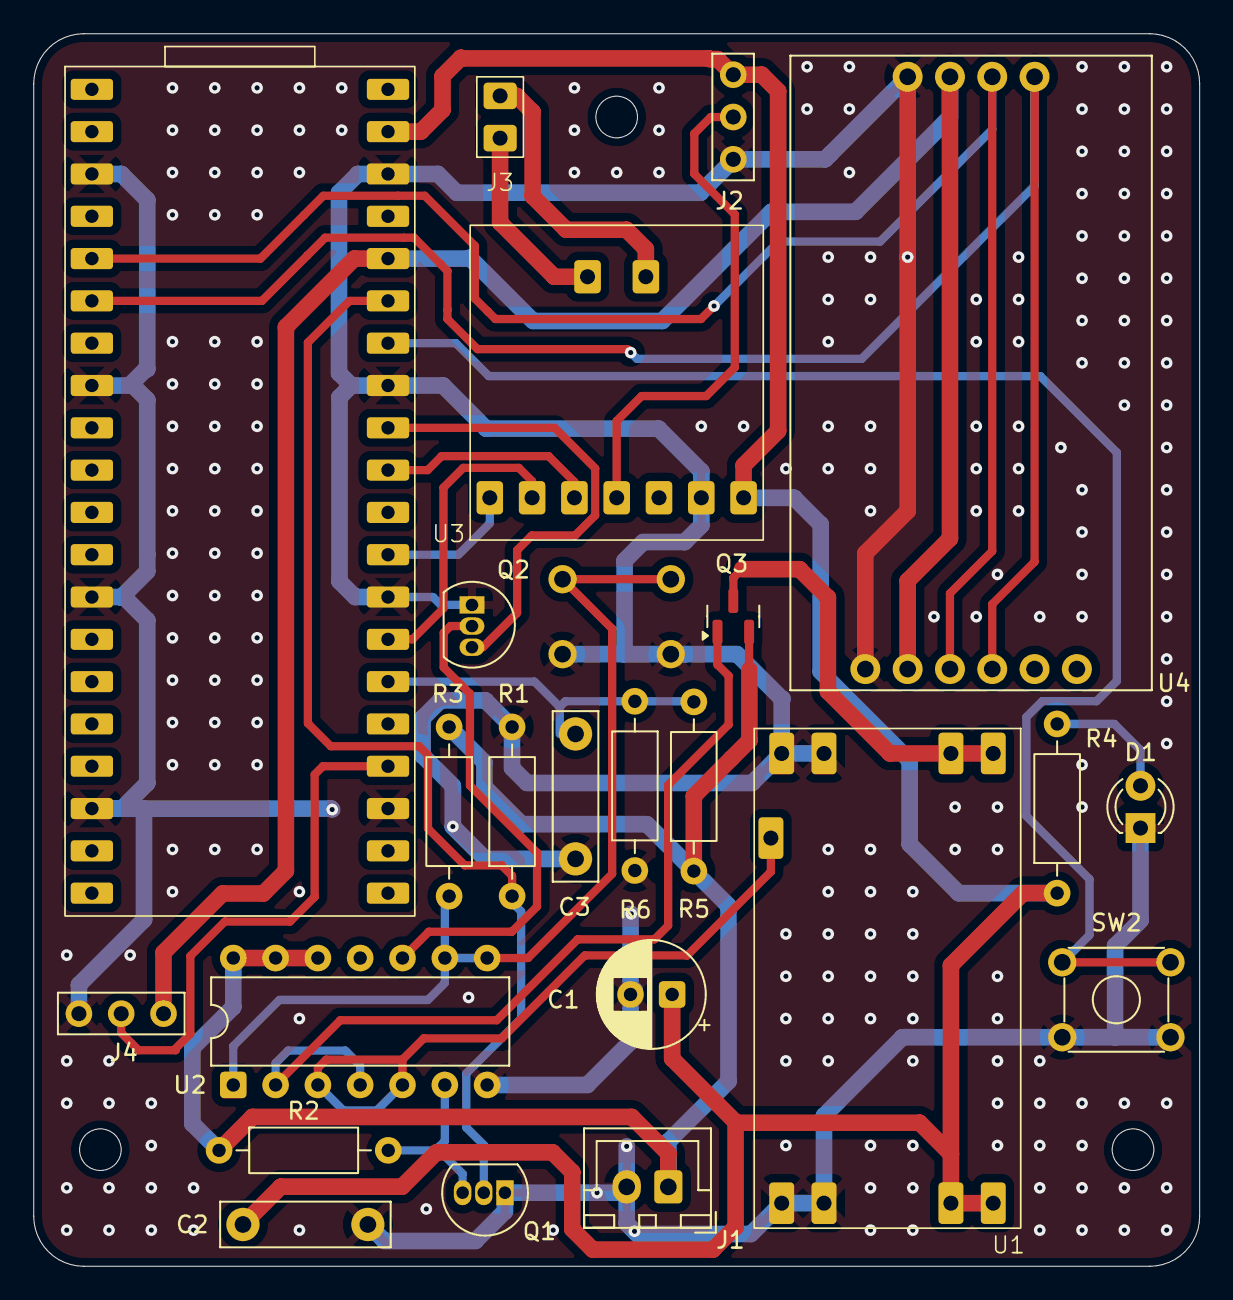
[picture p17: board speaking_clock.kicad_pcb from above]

Board: 2 copper layers, 70.0 x 74.0 mm, 24 parts (1 on the bottom side), 24 nets.

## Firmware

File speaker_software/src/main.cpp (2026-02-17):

#include <Arduino.h>

#include "board_pins.h"
#include "project_config.h"

#include <AudioFileSourceFS.h>
#include <AudioGeneratorMP3.h>
#include <AudioOutputI2S.h>
#include <LittleFS.h>

#include "rtc_ds3231.h"
#include "time_speech.h"
#include "date_speech.h"
#include "datetime_util.h"
#include "wifi_portal.h"
#include "app_state.h"
#include "serial_cli.h"

#if ENABLE_SERIAL_DEBUG
#define DBG_BEGIN(...) Serial.begin(__VA_ARGS__)
#define DBG_WAIT_FOR_SERIAL(ms) do { \
  const unsigned long _start = millis(); \
  while (!Serial && (millis() - _start) < (ms)) { delay(10); } \
} while (0)
#define DBG_PRINT(...) Serial.print(__VA_ARGS__)
#define DBG_PRINTLN(...) Serial.println(__VA_ARGS__)
#define DBG_PRINTF(...) Serial.printf(__VA_ARGS__)
#else
#define DBG_BEGIN(...)
#define DBG_WAIT_FOR_SERIAL(ms)
#define DBG_PRINT(...)
#define DBG_PRINTLN(...)
#define DBG_PRINTF(...)
#endif

RtcDs3231 g_rtc;
bool g_fs_ok = false;
TimeSpeech g_time_speech;
DateSpeech g_date_speech;
AudioOutputI2S* g_out = nullptr;
WifiPortal g_wifi_portal;
hw_timer_t* g_gain_timer = nullptr;
volatile bool g_gain_update_due = false;

uint32_t rtc_to_epoch_utc(const RtcDateTime& utc_dt) {
  const int y = static_cast<int>(utc_dt.year);
  const int m = static_cast<int>(utc_dt.month);
  const int d = static_cast<int>(utc_dt.day);

  auto is_leap = [](int year) {
    return (year % 4 == 0) && ((year % 100 != 0) || (year % 400 == 0));
  };
  static const uint8_t kDays[] = {31,28,31,30,31,30,31,31,30,31,30,31};

  int days = 0;
  for (int year = 1970; year < y; ++year) {
    days += is_leap(year) ? 366 : 365;
  }
  for (int month = 1; month < m; ++month) {
    days += (month == 2 && is_leap(y)) ? 29 : kDays[month - 1];
  }
  days += (d - 1);

  const int seconds =
      days * 86400 +
      static_cast<int>(utc_dt.hour) * 3600 +
      static_cast<int>(utc_dt.minute) * 60 +
      static_cast<int>(utc_dt.second);
  return static_cast<uint32_t>(seconds);
}

bool rtc_now_cb(uint32_t* epoch_utc, const char** tz_posix) {
  if (!epoch_utc || !tz_posix) return false;
  RtcDateTime rtc_dt{};
  if (!g_rtc.read_datetime(&rtc_dt)) return false;
  *epoch_utc = rtc_to_epoch_utc(rtc_dt);
  *tz_posix = kTimeZonePosix;
  return true;
}

void IRAM_ATTR on_gain_timer() {
  g_gain_update_due = true;
}

float read_battery_adc_voltage() {
  const int raw = analogRead(kPinBatteryAdc);
  return (static_cast<float>(raw) / 4095.0f) * 3.3f;
}

float read_battery_voltage() {
  const float v_adc = read_battery_adc_voltage();
  float a = 0.0f;
  float b = kBatteryVoltageScale;
  float c = 0.0f;
  get_battery_calibration(&a, &b, &c);
  return a * v_adc * v_adc + b * v_adc + c;
}

float read_volume_gain() {
  const int raw = analogRead(kPinVolumePotAdc);
  const float norm = static_cast<float>(raw) / 4095.0f;
  return kMp3GainMin + (kMp3GainMax - kMp3GainMin) * norm;
}

void set_rtc_from_browser(uint64_t epoch_ms, int16_t tz_offset_min) {
  (void)tz_offset_min;
  const uint32_t utc_sec = static_cast<uint32_t>(epoch_ms / 1000LL);
  const DateTime dt(utc_sec);
  g_rtc.set_datetime(dt.year(), dt.month(), dt.day(), dt.hour(), dt.minute(), dt.second());
  DBG_PRINTF("RTC set to %04u-%02u-%02u %02u:%02u:%02u\n",
             dt.year(), dt.month(), dt.day(), dt.hour(), dt.minute(), dt.second());
}

bool play_mp3_file(const char* path);
void play_wifi_on() {
  play_mp3_file("/mp3/wifi_on.mp3");
}

void speak_time_once() {
  digitalWrite(kPinPowerOff, LOW);
  RtcDateTime rtc_dt{};
  if (!g_rtc.read_datetime(&rtc_dt)) {
    DBG_PRINTLN("RTC read failed");
    return;
  }
  const RtcDateTime local = to_local_time(rtc_dt);
  const char* playlist[4] = {};
  const size_t count = g_time_speech.build_playlist_lang(local, current_language(), playlist, 4);
  for (size_t i = 0; i < count; ++i) {
    DBG_PRINT("Play: ");
    DBG_PRINTLN(playlist[i]);
    play_mp3_file(playlist[i]);
  }
}

void speak_date_once() {
  RtcDateTime rtc_dt{};
  if (!g_rtc.read_datetime(&rtc_dt)) {
    DBG_PRINTLN("RTC read failed");
    return;
  }
  const RtcDateTime local = to_local_time(rtc_dt);
  const char* playlist[6] = {};
  const size_t count = g_date_speech.build_playlist_lang(local, current_language(), playlist, 6);
  if (current_language() == SpeechLanguage::kEnglish && count > 0) {
    play_mp3_file(playlist[0]);
    delay(100);
    for (size_t i = 1; i < count; ++i) {
      play_mp3_file(playlist[i]);
    }
  } else {
    for (size_t i = 0; i < count; ++i) {
      play_mp3_file(playlist[i]);
    }
  }
}

bool play_mp3_file(const char* path) {
  if (!path || !g_fs_ok) return false;
  if (!LittleFS.exists(path)) {
    DBG_PRINT("Missing: ");
    DBG_PRINTLN(path);
    return false;
  }
  DBG_PRINT("Open: ");
  DBG_PRINTLN(path);
  AudioFileSourceFS file(LittleFS, path);
  AudioGeneratorMP3 mp3;
  if (!g_out) return false;
  if (!mp3.begin(&file, g_out)) {
    DBG_PRINT("MP3 begin failed: ");
    DBG_PRINTLN(path);
    return false;
  }
  while (mp3.isRunning()) {
    if (g_gain_update_due) {
      g_gain_update_due = false;
      if (g_out) {
        g_out->SetGain(read_volume_gain());
      }
    }
    if (!mp3.loop()) mp3.stop();
    delay(1);
  }
  return true;
}

void list_littlefs_root() {
  File root = LittleFS.open("/", "r");
  if (!root) {
    DBG_PRINTLN("LittleFS root open failed");
    return;
  }
  DBG_PRINTLN("LittleFS listing:");
  File f = root.openNextFile();
  while (f) {
    DBG_PRINT(" - ");
    DBG_PRINT(f.name());
    if (!f.isDirectory()) {
      DBG_PRINT(" (");
      DBG_PRINT(f.size());
      DBG_PRINT(" bytes)");
    }
    DBG_PRINTLN();
    f = root.openNextFile();
  }
  root.close();
}

void setup() {
  DBG_BEGIN(115200);
  DBG_WAIT_FOR_SERIAL(2000);
  DBG_PRINTLN("Speaking Clock boot");

  if (!g_rtc.begin()) {
    DBG_PRINTLN("RTC init failed");
  }

  g_fs_ok = LittleFS.begin(false);
  if (!g_fs_ok) {
    DBG_PRINTLN("LittleFS init failed");
  } else {
    DBG_PRINTLN("LittleFS init OK");
    list_littlefs_root();
    app_state_begin(g_fs_ok);
  }

  g_wifi_portal.begin();
  g_wifi_portal.set_rtc_callback(set_rtc_from_browser);
  g_wifi_portal.set_rtc_now_callback(rtc_now_cb);
  g_wifi_portal.set_battery_callback(read_battery_voltage);

  g_out = new AudioOutputI2S();
  g_out->SetPinout(kPinI2sBclk, kPinI2sLrc, kPinI2sData);
  g_out->SetChannels(1);
  g_out->SetOutputModeMono(true);
  g_out->SetGain(read_volume_gain());

  pinMode(kPinTriggerButton, INPUT_PULLUP);
  pinMode(kPinConfigButton, INPUT_PULLUP);
  pinMode(kPinBatteryAdc, INPUT);
  pinMode(kPinVolumePotAdc, INPUT);
  pinMode(kPinPowerOff, OUTPUT);
  digitalWrite(kPinPowerOff, LOW);
  
  DBG_PRINTF("Flash size: %u bytes\n", ESP.getFlashChipSize());
  DBG_PRINTF("PSRAM size: %u bytes\n", ESP.getPsramSize());

  g_gain_timer = timerBegin(0, 80, true);
  if (g_gain_timer) {
    timerAttachInterrupt(g_gain_timer, &on_gain_timer, true);
    timerAlarmWrite(g_gain_timer, 200000, true);
    timerAlarmEnable(g_gain_timer);
  }

  const bool cfg_pressed = (digitalRead(kPinConfigButton) == LOW);
  if (cfg_pressed) {
    play_wifi_on();
    g_wifi_portal.start();
  } else {
    uint32_t prev_epoch = 0;
    const bool has_prev = load_last_time(&prev_epoch);
    RtcDateTime rtc_dt{};
    if (g_rtc.read_datetime(&rtc_dt)) {
      const uint32_t now_epoch = rtc_to_epoch_utc(rtc_dt);
      const uint32_t diff = has_prev ? (now_epoch - prev_epoch) : 0;
      DBG_PRINTF("Time delta (startup) = %u s\n", diff);
      const bool do_date = has_prev && (diff <= 20);
      speak_time_once();
      if (do_date) {
        delay(500);
        speak_date_once();
      }
      save_last_time(now_epoch);
      digitalWrite(kPinPowerOff, HIGH);
    }
  }
}

void loop() {
  static int prev_time_state = HIGH;
  const int time_state = digitalRead(kPinTriggerButton);

  if (prev_time_state == HIGH && time_state == LOW) {
    DBG_PRINTLN("Button: TIME");
    uint32_t prev_epoch = 0;
    const bool has_prev = load_last_time(&prev_epoch);
    RtcDateTime rtc_dt{};
    if (g_rtc.read_datetime(&rtc_dt)) {
      const uint32_t now_epoch = rtc_to_epoch_utc(rtc_dt);
      const uint32_t diff = has_prev ? (now_epoch - prev_epoch) : 0;
      DBG_PRINTF("Time delta (trigger) = %u s\n", diff);
      const bool do_date = has_prev && (diff <= 20);
      speak_time_once();
      if (do_date) {
        delay(500);
        speak_date_once();
      }
      save_last_time(now_epoch);
      digitalWrite(kPinPowerOff, HIGH);
    }
  }

  prev_time_state = time_state;

  serial_cli_handle(g_time_speech,
                    g_date_speech,
                    g_fs_ok,
                    play_mp3_file,
                    current_language,
                    set_language,
                    read_battery_voltage,
                    read_battery_adc_voltage);
  g_wifi_portal.loop();
}

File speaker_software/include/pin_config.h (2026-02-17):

#pragma once

// Default pin configuration for a breadboard setup on ESP32-S3.
// Adjust as needed once wiring is finalized.

// I2C (DS3231) - keep away from ADC pins
constexpr int kPinI2cSda = 14;
constexpr int kPinI2cScl = 15;

// I2S (MAX98357A)
constexpr int kPinI2sBclk = 5;
constexpr int kPinI2sLrc  = 6;
constexpr int kPinI2sData = 7;

// Trigger button (active low)
constexpr int kPinTriggerButton = 8;

// Config button (active low)
constexpr int kPinConfigButton = 9;

// Power-off control (active high)
constexpr int kPinPowerOff = 10;

// Battery voltage ADC input (adjust as needed)
constexpr int kPinBatteryAdc = 4;

// Volume potentiometer ADC input (0..3.3V)
constexpr int kPinVolumePotAdc = 1;

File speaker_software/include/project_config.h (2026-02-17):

#pragma once

// Global project configuration (ESP32-S3 build)

// Audio
// I2S output sample rate
constexpr int kAudioOutputSampleRateHz = 48000;
// MP3 output gain range (0.0 .. 1.0 recommended)
constexpr float kMp3GainMin = 0.1f;
constexpr float kMp3GainMax = 1.0f;
// Speech language selection
enum class SpeechLanguage : uint8_t {
  kGerman = 0,
  kEnglish = 1,
};
constexpr SpeechLanguage kSpeechLanguage = SpeechLanguage::kGerman;
// Base paths for audio files in LittleFS (MP3 files).
constexpr const char* kAudioBasePathDe = "/mp3";
constexpr const char* kAudioBasePathEn = "/mp3_en";
inline const char* audio_base_path_for(SpeechLanguage lang) {
  return (lang == SpeechLanguage::kEnglish) ? kAudioBasePathEn : kAudioBasePathDe;
}
inline const char* audio_base_path() {
  return audio_base_path_for(kSpeechLanguage);
}

// Debug serial logging (can be overridden via build flag)
#ifndef ENABLE_SERIAL_DEBUG
#define ENABLE_SERIAL_DEBUG 1
#endif

// Timezone / DST configuration
// RTC runs on UTC; local time is derived via POSIX TZ string.
constexpr bool kRtcIsUtc = true;
constexpr const char* kTimeZonePosix = "CET-1CEST,M3.5.0/02,M10.5.0/03";
constexpr int kTimeZoneOffsetMinutes = 60; // CET default (fallback)
constexpr bool kEnableEuDst = true;        // fallback rule if POSIX TZ is empty

// Software clock start (used while RTC is disconnected)
constexpr uint16_t kSoftStartYear = 2026;
constexpr uint8_t kSoftStartMonth = 1;
constexpr uint8_t kSoftStartDay = 29;
constexpr uint8_t kSoftStartHour = 13;
constexpr uint8_t kSoftStartMinute = 58;
constexpr uint8_t kSoftStartSecond = 0;

// RTC
constexpr int kRtcI2cFrequencyHz = 100000;

// WiFi / Web
constexpr const char* kWifiApSsid = "SpeakingClock";
constexpr const char* kWifiHostname = "clock";
constexpr uint32_t kWifiConnectTimeoutMs = 10000;
constexpr uint16_t kWifiConfigPortalTimeoutSec = 180;

// Battery measurement (ADC)
constexpr float kBatteryVoltageScale = 1.68f; // 68k/100k divider, measure across 100k

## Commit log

2026-02-17 Initial snapshot
    [bom.csv, bottom_case.stl, clip.stl, designators.csv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]
2026-02-17 update pcb production data
    [bom.csv, designators.csv, positions.csv, speaking_clock.kicad_pcb]
2026-02-17 update STL files
    [bottom_case.stl, clip1.stl, clip2.stl, top_case.stl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]
2026-02-22 smd electronics added
    [ESP32_S3_MCU.kicad_sch, bom.csv, designators.csv, other.kicad_sch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]
2026-02-27 take over changes to electronics from test branch
    [ESP32_S3_MCU.kicad_sch, bom.csv, bom.xlsx, designators.csv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]
